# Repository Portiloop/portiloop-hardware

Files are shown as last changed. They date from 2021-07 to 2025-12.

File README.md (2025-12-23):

# Portiloop hardware

This repository documents hardware implementations of the `Portiloop` device. 
Which is a portable EEG closed-loop stimulation device.
[The software repository](https://github.com/Portiloop/portiloop-software) enables controlling the device from a simple Graphical User Interface (GUI).

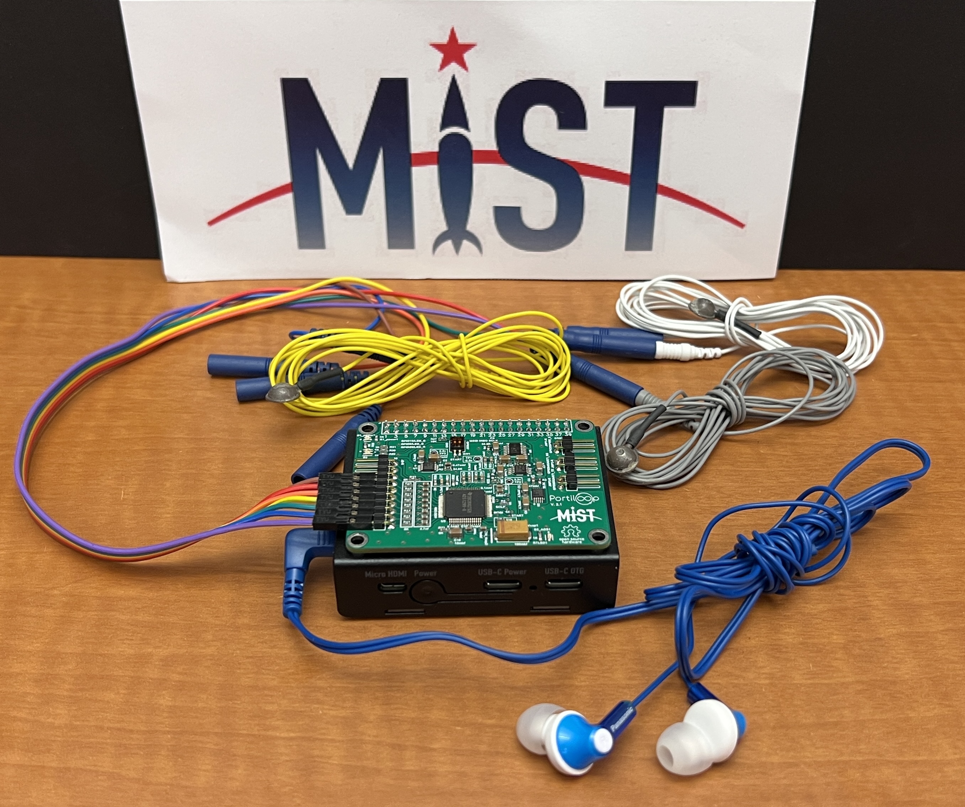
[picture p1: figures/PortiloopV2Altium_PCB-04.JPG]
mainImage


The last hardware iteration of the `Portiloop` device consists of a PCB built around an [ADS1299 chip](https://www.ti.com/product/ADS1299) 
with connectors for a [Coral Dev Board Mini](https://coral.ai/products/dev-board-mini/#documentation).
The `ADS1299` is an ADC responsible for processing analog EEG signal.

This repository open-sources all relevant plans for building this implementation.

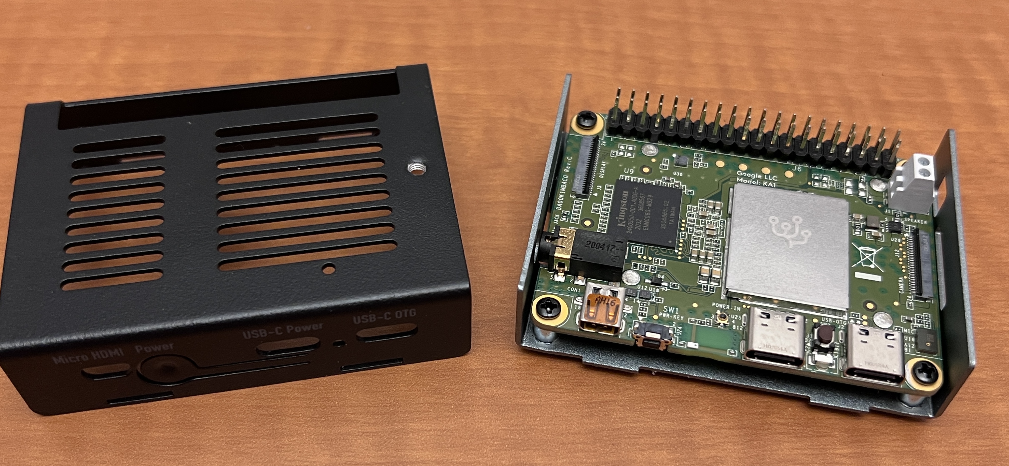
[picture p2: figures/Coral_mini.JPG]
coralMini

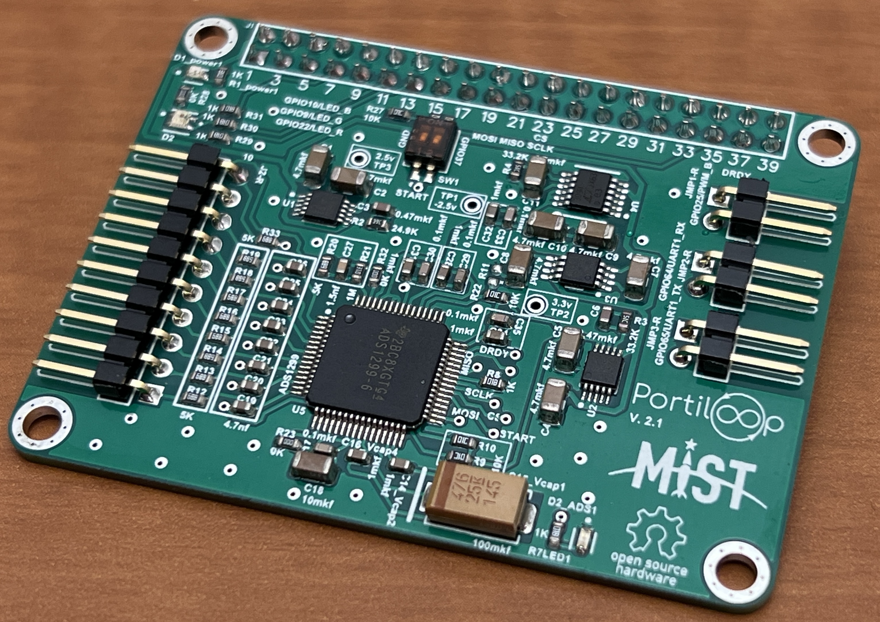
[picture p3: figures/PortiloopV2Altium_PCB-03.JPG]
v2.3

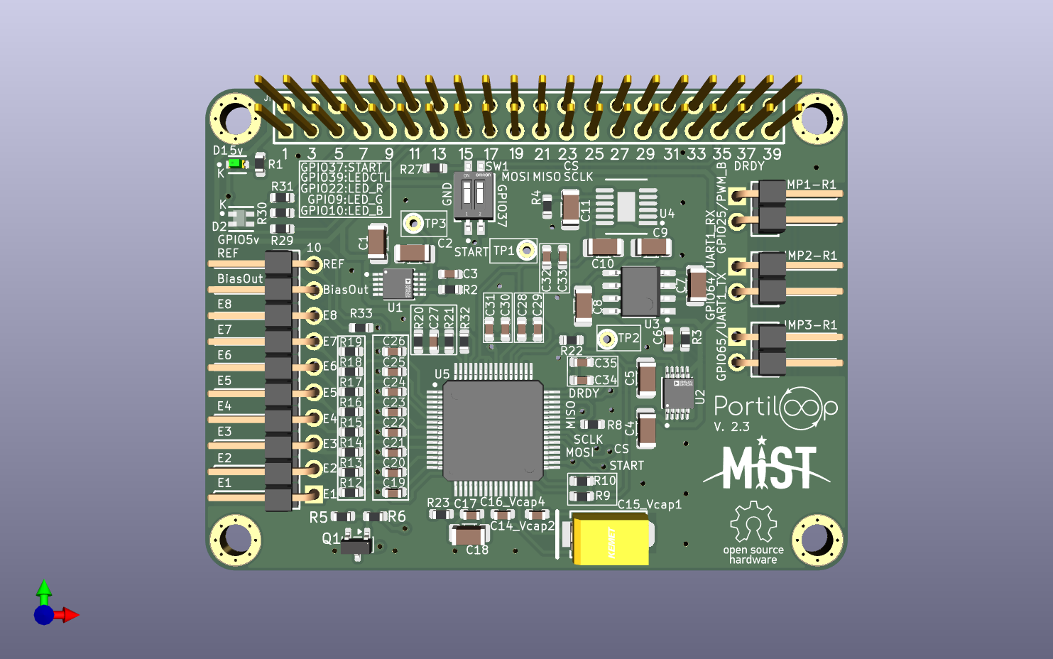
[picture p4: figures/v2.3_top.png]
top

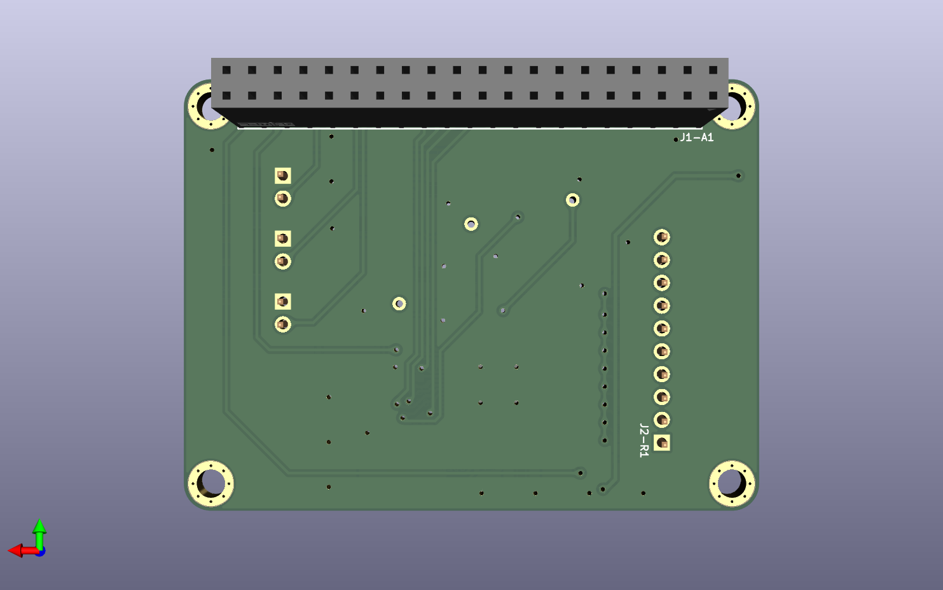
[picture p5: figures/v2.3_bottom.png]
back

video

To view the full interactive 3D model, click below:

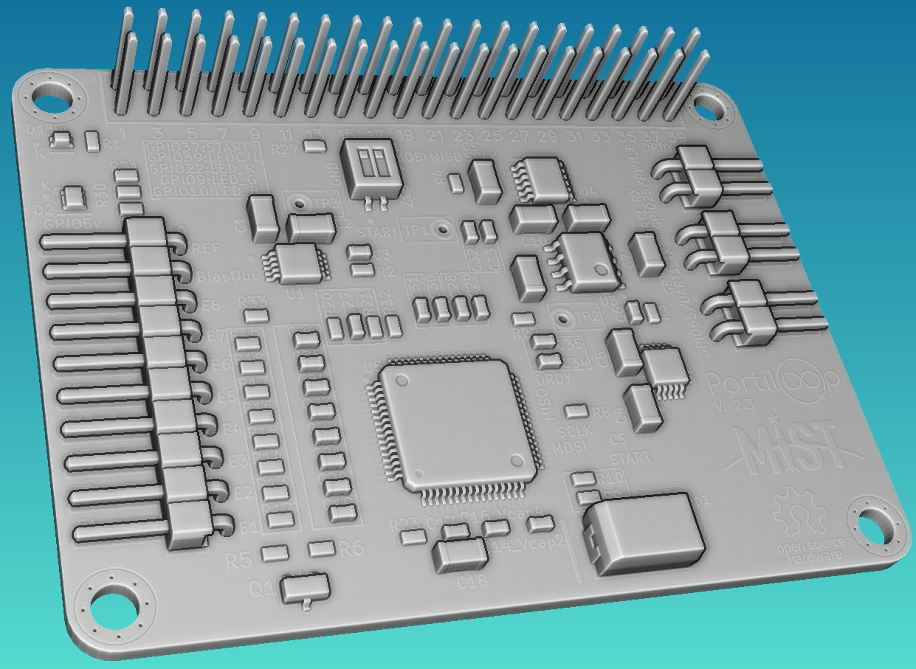
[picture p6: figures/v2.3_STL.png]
3D Preview Portiloop

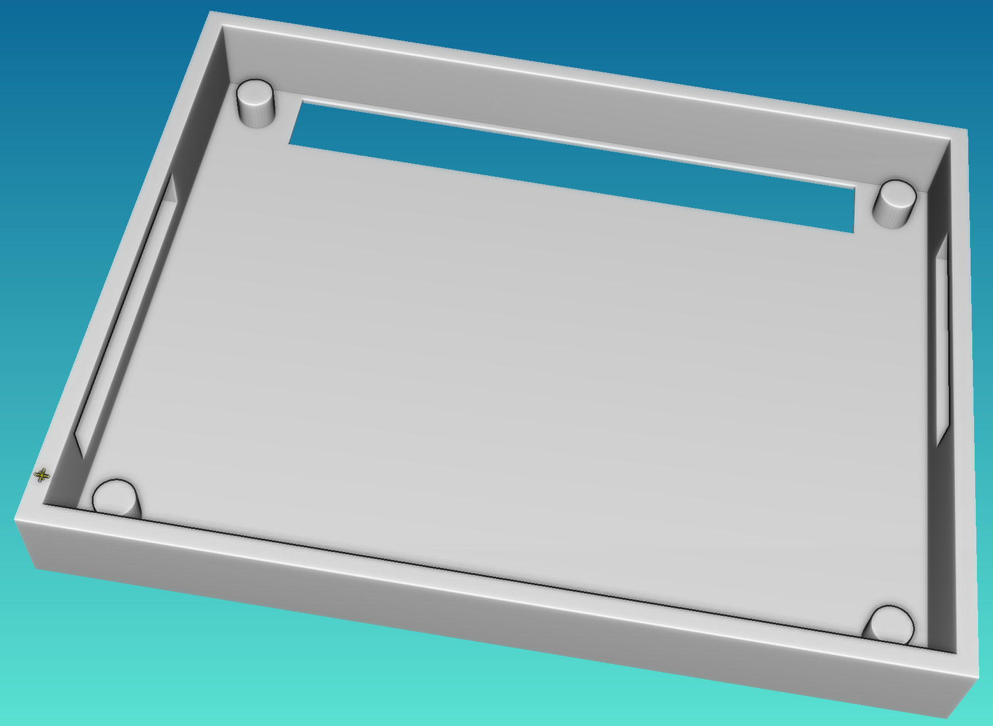
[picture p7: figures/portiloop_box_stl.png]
3D Preview Box

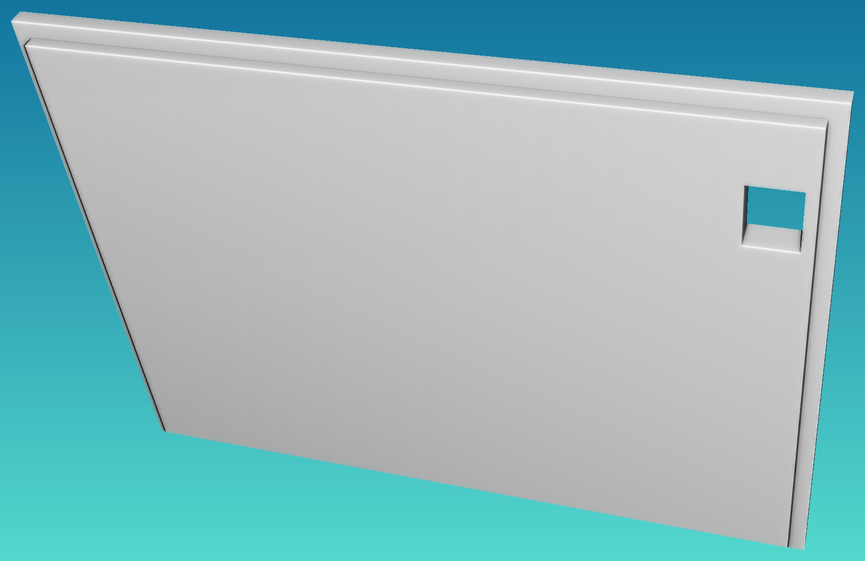
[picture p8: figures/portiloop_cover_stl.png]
3D Preview Box Cover

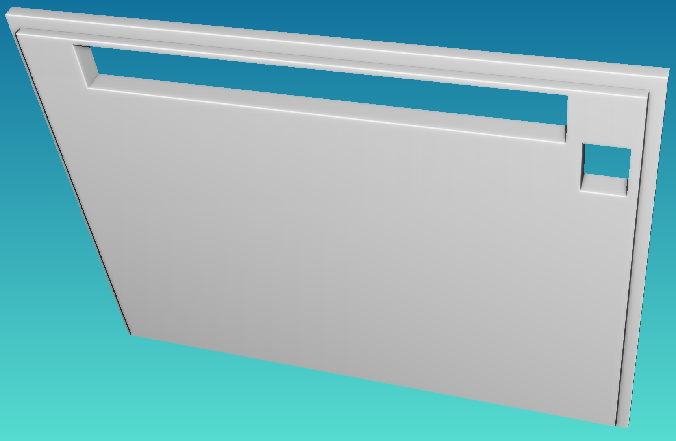
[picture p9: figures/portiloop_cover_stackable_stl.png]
3D Preview Box Cover Stackable


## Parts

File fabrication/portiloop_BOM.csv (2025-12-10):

Id | Designator | Footprint | Quantity | Designation | Part #
1 | C10,C1,C5,C4,C2,C9,C11 | 3216[1206]_cap | 7 | 4.7uF | CL31B475KBHNNNE
2 | C15_Vcap1 | KEMT-T491-D_M | 1 | 100uF | T491D107K016AT
3 | C16_Vcap4,C34,C31,C14_Vcap2,C32,C28 | 1608[0603]_cap | 6 | 1uF | CC0603KRX5R8BB105
4 | C18 | 3216[1206]_cap | 1 | 10uF | CC1206KKX7R8BB106
5 | C21,C26,C22,C20,C23,C19,C25,C24 | 1608[0603]_cap | 8 | 4.7nf | CC0603KRX7R9BB472
6 | C27 | 1608[0603]_cap | 1 | 1.5nf | CC0603KRX7R9BB152
7 | C35,C17,C33,C29,C30 | 1608[0603]_cap | 5 | 0.1uF | CC0603KRX7R9BB104
8 | C6,C3 | 1608[0603]_cap | 2 | 0.47uf | CC0603KRX7R9BB474
9 | C8,C7 | 3216[1206]_cap | 2 | 47uF | GRM31CR60J476ME19L
10 | D2 | FP-APTF1616SEJ3ZGGVBDC-MFG | 1 | APTF1616SEJ3ZGGVBDC
11 | D1 | FP-LTST-C190GKT-MFG | 1 | LTST-C190GKT
12 | J1-A1 | FP-SSQ-120-03-G-D-MFG | 1 | SSQ-120-03-G-D
13 | J2-R1 | 61301011021 | 1 | 61301011021
14 | JMP1-R1,JMP2-R1,JMP3-R1 | 61300211021 | 3 | 61300211021
15 | M2,M4,M3,M1 | board_screw | 4 | DNP | DNP
16 | Q1 | SOT-23 | 1 | IRLML2502 | IRLML2502TRPBF
17 | R1 | 1608[0603]_res | 1 | 1K | RC0603FR-071KL
18 | R12,R19,R33,R14,R18,R20,R16,R17,R15,R13 | 1608[0603]_res | 10 | 5K OR 4.99K | RC0603FR-074K99L
19 | R21 | 1608[0603]_res | 1 | 1M | RC0603FR-071ML
20 | R29 | 1608[0603]_res | 1 | 1.5K | RC0603FR-071K5L
21 | R3 | 1608[0603]_res | 1 | 33.2K | RC0603FR-0733K2L
22 | R30 | 1608[0603]_res | 1 | 6K OR 6.04K | RC0603FR-076K04L
23 | R31 | 1608[0603]_res | 1 | 1.8K | RC0603FR-071K8L
24 | R32,R23 | 1608[0603]_res | 2 | 0 | RC0603FR-070RL
25 | R4,R2 | 1608[0603]_res | 2 | 24.9K | RC0603FR-0724K9L
26 | R5 | 1608[0603]_res | 1 | 100K | 0603SAJ0104T5E
27 | R6 | 1608[0603]_res | 1 | 100 | RC0603JR-07100RL
28 | R8,R9,R10,R22,R27 | 1608[0603]_res | 5 | 10K | RC0603FR-0710KL
29 | SW1 | FP-A6H-2102-MFG | 1 | A6H-2102
30 | TP1,TP2,TP3 | TESTPOINT | 1 | DNP | DNP
31 | U2,U1 | FP-MSE-10-05-08-1664-IPC_C | 2 | LT3042xMSE | LT3042EMSE#PBF
32 | U3 | D0008A_M | 1 | LM2662MX/NOPB | LM2662MX/NOPB
33 | U4 | FP-MSE-12-05-08-1666-IPC_A | 1 | LT3094xMSE | LT3094EMSE#PBF
34 | U5 | PAG0064A_M | 1 | ADS1299IPAG

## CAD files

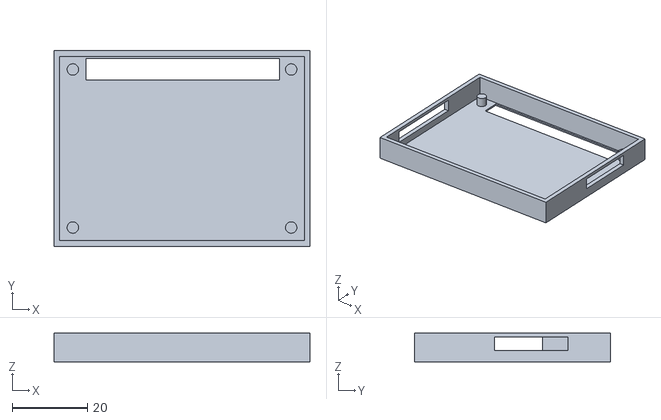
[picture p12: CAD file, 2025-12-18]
models/portiloop_box.stl
68.0 x 52.0 x 7.69

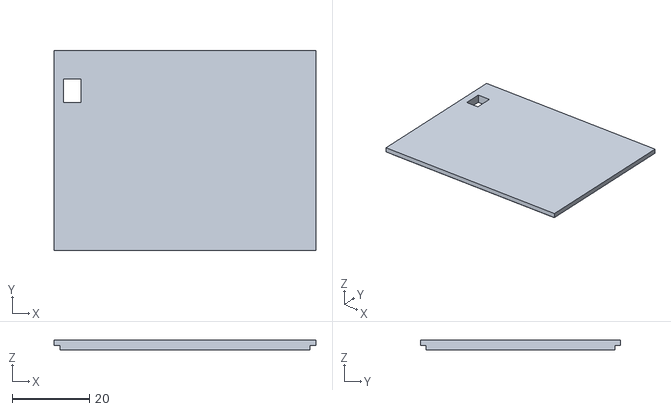
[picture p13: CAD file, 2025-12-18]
models/portiloop_cover.stl
68.0 x 52.0 x 2.65

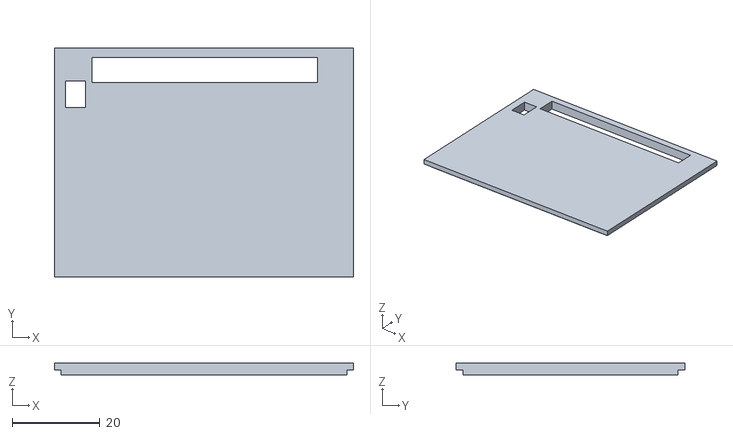
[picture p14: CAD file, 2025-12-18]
models/portiloop_cover_ stackable.stl
68.0 x 52.0 x 2.65

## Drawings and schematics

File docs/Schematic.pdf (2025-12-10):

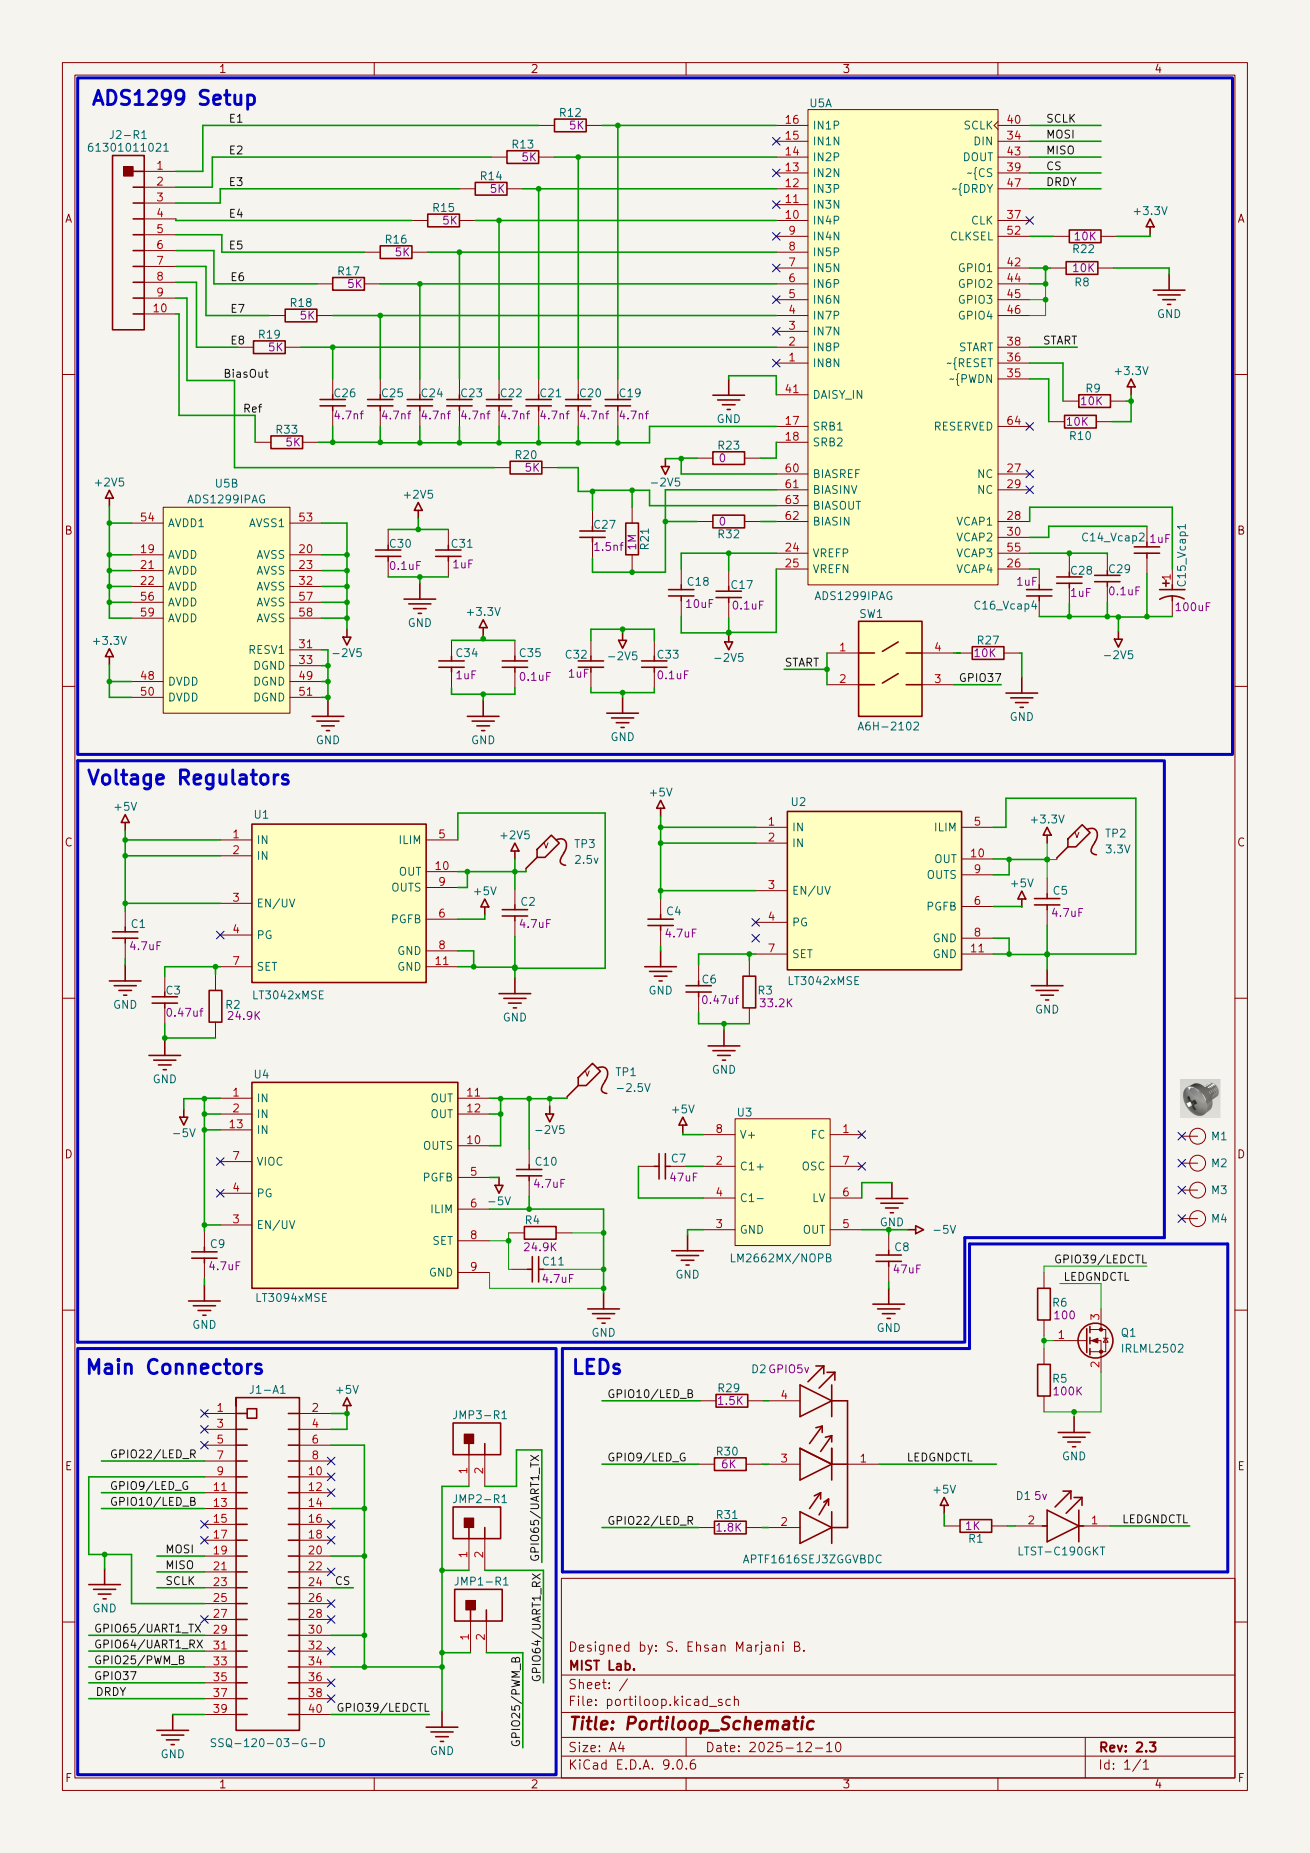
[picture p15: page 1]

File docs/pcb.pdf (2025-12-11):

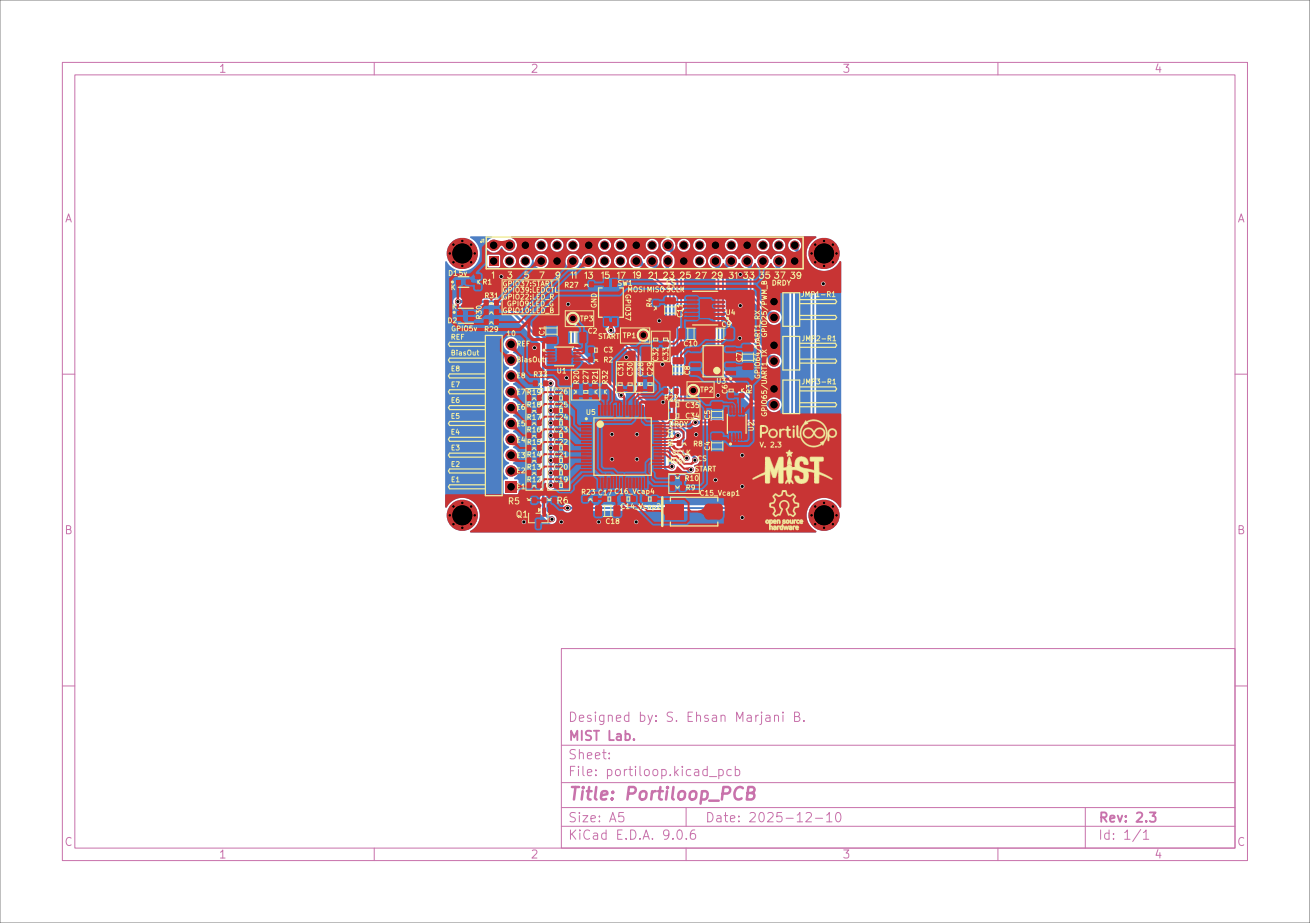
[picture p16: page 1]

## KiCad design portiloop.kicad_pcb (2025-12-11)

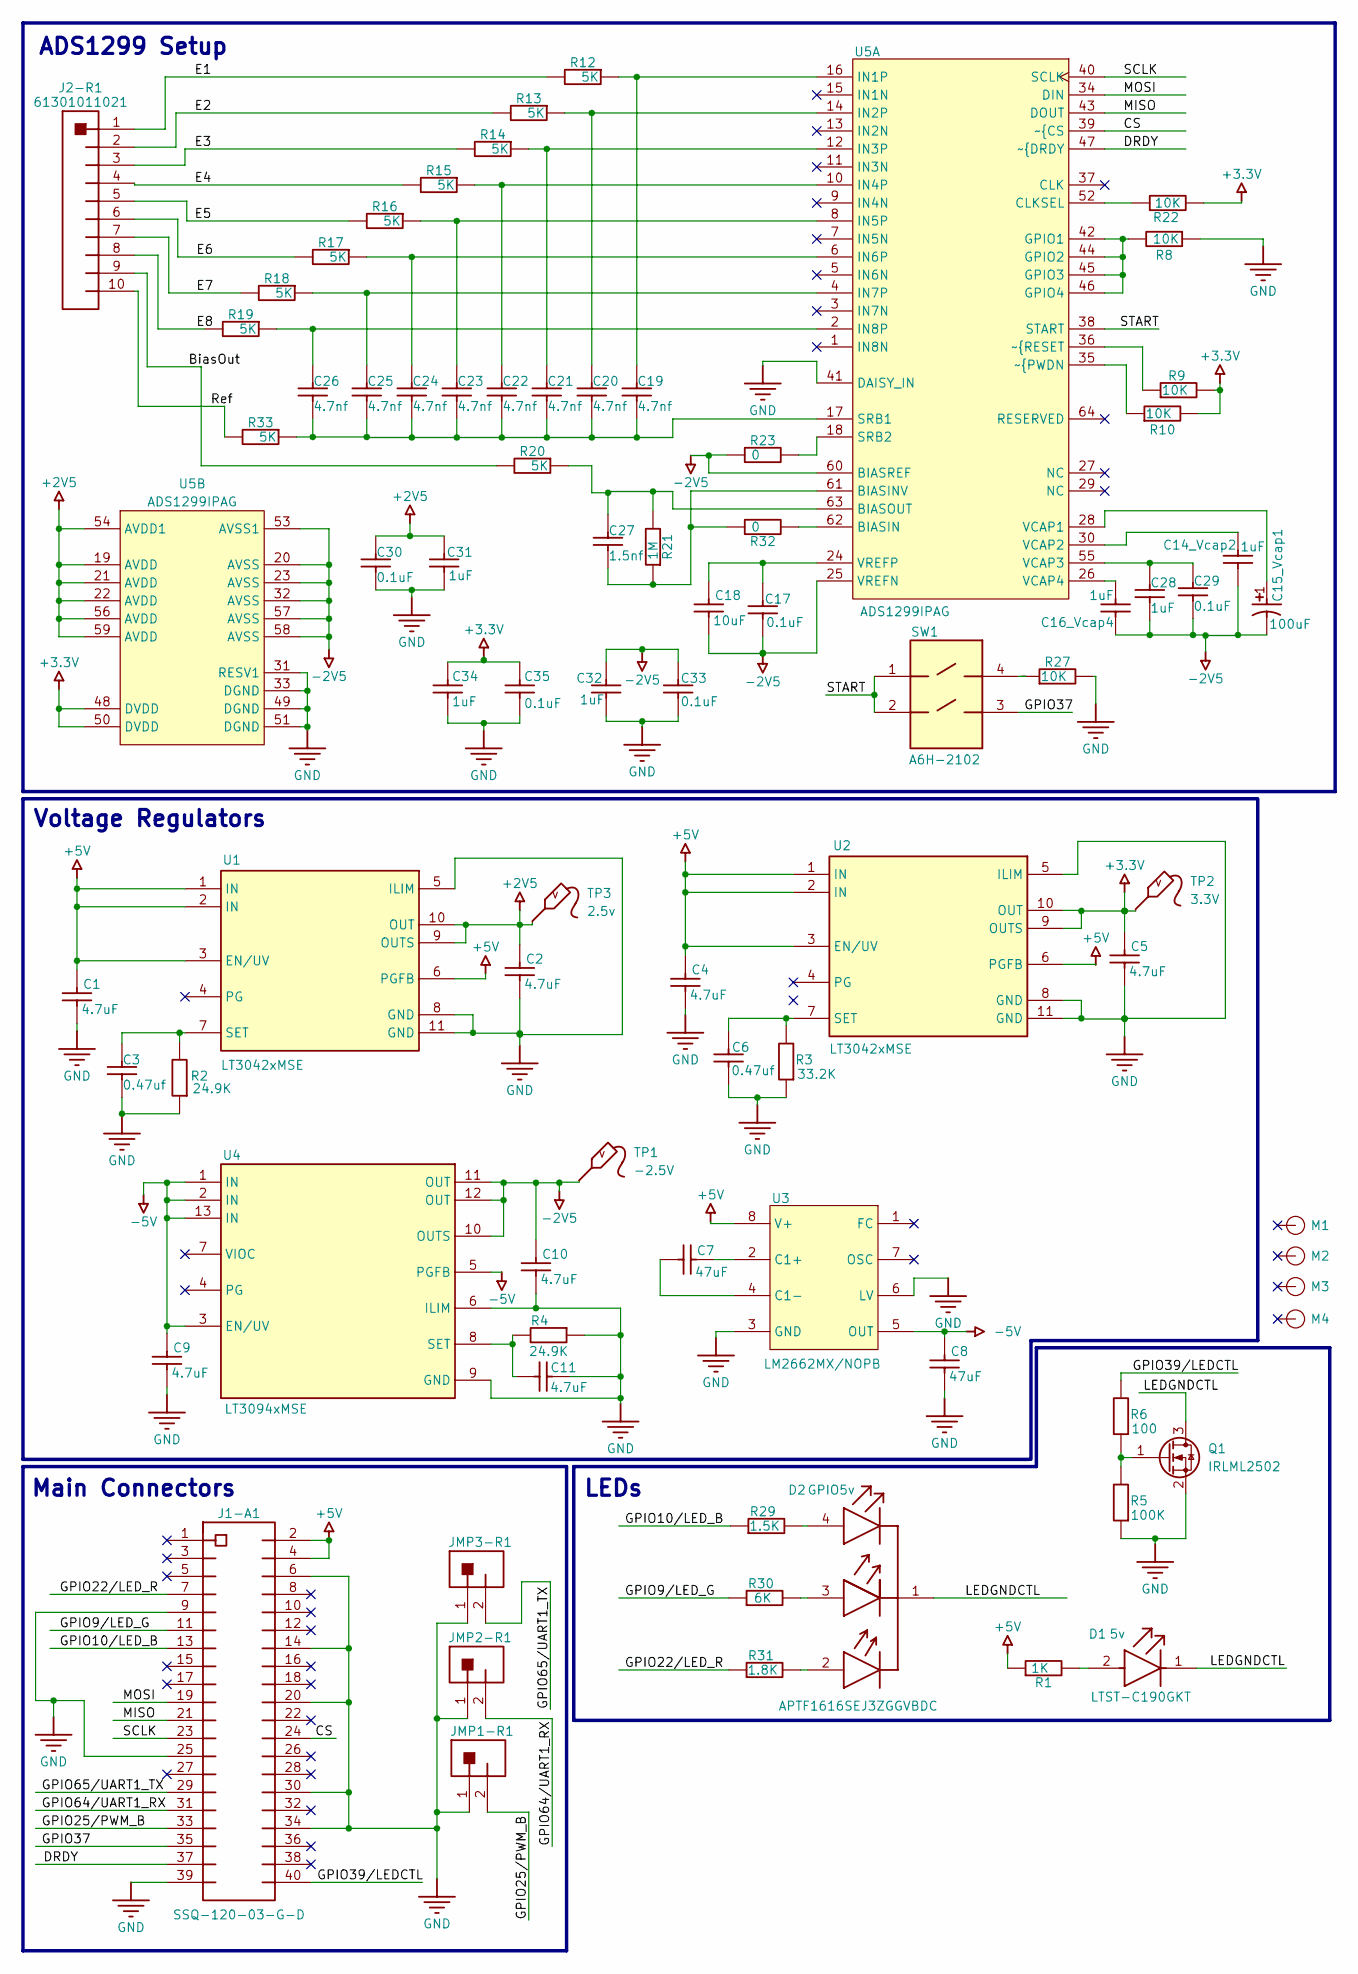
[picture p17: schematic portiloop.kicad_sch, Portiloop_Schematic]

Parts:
C1, C2, C4, C5, C9, C10, C11: 4.7uF; 3216[1206]_cap_3d
C3, C6: 0.47uf; 1608[0603]_cap_3d
C7, C8: 47uF; 3216[1206]_cap_3d
C14_Vcap2, C16_Vcap4, C28, C31, C32, C34: 1uF; 1608[0603]_cap_3d
C15_Vcap1: 100uF; KEMT-T491-D_M
C17, C29, C30, C33, C35: 0.1uF; 1608[0603]_cap_3d
C18: 10uF; 3216[1206]_cap_3d
C19, C20, C21, C22, C23, C24, C25, C26: 4.7nf; 1608[0603]_cap_3d
C27: 1.5nf; 1608[0603]_cap_3d
D1: LTST-C190GKT; FP-LTST-C190GKT-MFG
D2: APTF1616SEJ3ZGGVBDC; FP-APTF1616SEJ3ZGGVBDC-MFG
J1-A1: SSQ-120-03-G-D; FP-SSQ-120-03-G-D-MFG
J2-R1: 61301011021
JMP1-R1, JMP2-R1, JMP3-R1: 61300211021
M1, M2, M3, M4: board_screw
Q1: IRLML2502; SOT-23
R1: 1K; 1608[0603]_res_3d
R2, R4: 24.9K; 1608[0603]_res_3d
R3: 33.2K; 1608[0603]_res_3d
R5: 100K; 1608[0603]_res_3d
R6: 100; 1608[0603]_res_3d
R8, R22: 10k; 1608[0603]_res_3d
R9, R10, R27: 10K; 1608[0603]_res_3d
R12, R13, R14, R15, R16, R17, R18, R19, R20, R33: 5k; 1608[0603]_res_3d
R21: 1M; 1608[0603]_res_3d
R23, R32: 0; 1608[0603]_res_3d
R29: 1.5K; 1608[0603]_res_3d
R30: 6K; 1608[0603]_res_3d
R31: 1.8K; 1608[0603]_res_3d
SW1: A6H-2102; FP-A6H-2102-MFG
TP1: -2.5V; TESTPOINT
TP2: 3.3V; TESTPOINT
TP3: 2.5v; TESTPOINT
U1, U2: LT3042xMSE; FP-MSE-10-05-08-1664-IPC_C
U3: LM2662MX/NOPB; D0008A_M
U4: LT3094xMSE; FP-MSE-12-05-08-1666-IPC_A
U5: ADS1299IPAG; PAG0064A_M

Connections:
+2V5: C2.2, C30.2, C31.2, TP3.1 (T), U1.9 (OUTS), U1.10 (OUT), U5.19 (AVDD), U5.21 (AVDD), U5.22 (AVDD), U5.54 (AVDD1), U5.56 (AVDD), U5.59 (AVDD)
+3.3V: C5.2, C34.2, C35.2, R9.1, R10.1, R22.1, TP2.1 (T), U2.9 (OUTS), U2.10 (OUT), U5.48 (DVDD), U5.50 (DVDD)
+5V: C1.2, C4.2, J1-A1.2, J1-A1.4, R1.2, U1.1 (IN), U1.2 (IN), U1.3 (EN/UV), U1.6 (PGFB), U2.1 (IN), U2.2 (IN), U2.3 (EN/UV), U2.6 (PGFB), U3.8 (V+)
-2V5: C10.2, C14_Vcap2.1, C15_Vcap1.2, C16_Vcap4.1, C17.2, C18.1, C28.1, C29.1, C32.2, C33.2, R23.2, TP1.1 (T), U4.10 (OUTS), U4.11 (OUT), U4.12 (OUT), U5.20 (AVSS), U5.23 (AVSS), U5.25 (VREFN), U5.32 (AVSS), U5.53 (AVSS1), U5.57 (AVSS), U5.58 (AVSS), U5.60 (BIASREF)
-5V: C8.2, C9.2, U3.5 (OUT), U4.1 (IN), U4.2 (IN), U4.3 (EN/UV), U4.5 (PGFB), U4.13 (IN)
/BiasOut: J2-R1.9, R20.1
/CS: J1-A1.24, U5.39 (~{CS)
/DRDY: J1-A1.37, U5.47 (~{DRDY)
/E1: J2-R1.1, R12.1
/E2: J2-R1.2, R13.1
/E3: J2-R1.3, R14.1
/E4: J2-R1.4, R15.1
/E5: J2-R1.5, R16.1
/E6: J2-R1.6, R17.1
/E7: J2-R1.7, R18.1
/E8: J2-R1.8, R19.1
/GPIO9/LED_G: J1-A1.11, R30.2
/GPIO10/LED_B: J1-A1.13, R29.2
/GPIO22/LED_R: J1-A1.7, R31.2
/GPIO25/PWM_B: J1-A1.33, JMP1-R1.2
/GPIO37: J1-A1.35, SW1.3
/GPIO39/LEDCTL: J1-A1.40, R6.1
/GPIO64/UART1_RX: J1-A1.31, JMP2-R1.2
/GPIO65/UART1_TX: J1-A1.29, JMP3-R1.2
/LEDGNDCTL: D1.1 (C), D2.1 (COMMON_CATHODE), Q1.3 (D)
/MISO: J1-A1.21, U5.43 (DOUT)
/MOSI: J1-A1.19, U5.34 (DIN)
/Ref: J2-R1.10, R33.1
/SCLK: J1-A1.23, U5.40 (SCLK)
/START: SW1.1, SW1.2, U5.38 (START)
GND: C1.1, C2.1, C3.1, C4.1, C5.1, C6.2, C8.1, C9.1, C10.1, C11.1, C30.1, C31.1, C32.1, C33.1, C34.1, C35.1, J1-A1.6, J1-A1.9, J1-A1.14, J1-A1.20, J1-A1.25, J1-A1.30, J1-A1.34, J1-A1.39, JMP1-R1.1, JMP2-R1.1, JMP3-R1.1, Q1.2 (S), R2.2, R3.2, R4.2, R5.2, R8.2, R27.1, U1.5 (ILIM), U1.8 (GND), U1.11 (GND), U2.5 (ILIM), U2.8 (GND), U2.11 (GND), U3.3 (GND), U3.6 (LV), U4.6 (ILIM), U4.9 (GND), U5.31 (RESV1), U5.33 (DGND), U5.41 (DAISY_IN), U5.49 (DGND), U5.51 (DGND)
unnamed: D1.2 (A), R1.1
unnamed: D2.4 (BLUE_A), R29.1
unnamed: D2.3 (GREEN_A), R30.1
unnamed: D2.2 (RED_A), R31.1
unnamed: Q1.1 (G), R5.1, R6.2
unnamed: R27.2, SW1.4
unnamed: C3.2, R2.1, U1.7 (SET)
unnamed: C6.1, R3.1, U2.7 (SET)
unnamed: C7.2, U3.2 (C1+)
unnamed: C7.1, U3.4 (C1-)
unnamed: C11.2, R4.1, U4.8 (SET)
unnamed: R32.1, U5.62 (BIASIN)
unnamed: C27.1, R21.2, R32.2, U5.61 (BIASINV)
unnamed: C27.2, R20.2, R21.1, U5.63 (BIASOUT)
unnamed: R22.2, U5.52 (CLKSEL)
unnamed: R8.1, U5.42 (GPIO1), U5.44 (GPIO2), U5.45 (GPIO3), U5.46 (GPIO4)
unnamed: C19.2, R12.2, U5.16 (IN1P)
unnamed: C20.2, R13.2, U5.14 (IN2P)
unnamed: C21.2, R14.2, U5.12 (IN3P)
unnamed: C22.2, R15.2, U5.10 (IN4P)
unnamed: C23.2, R16.2, U5.8 (IN5P)
unnamed: C24.2, R17.2, U5.6 (IN6P)
unnamed: C25.2, R18.2, U5.4 (IN7P)
unnamed: C26.2, R19.2, U5.2 (IN8P)
unnamed: C19.1, C20.1, C21.1, C22.1, C23.1, C24.1, C25.1, C26.1, R33.2, U5.17 (SRB1)
unnamed: R23.1, U5.18 (SRB2)
unnamed: C15_Vcap1.1, U5.28 (VCAP1)
unnamed: C14_Vcap2.2, U5.30 (VCAP2)
unnamed: C28.2, C29.2, U5.55 (VCAP3)
unnamed: C16_Vcap4.2, U5.26 (VCAP4)
unnamed: C17.1, C18.2, U5.24 (VREFP)
unnamed: R10.2, U5.35 (~{PWDN)
unnamed: R9.2, U5.36 (~{RESET)

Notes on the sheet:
Voltage Regulators
ADS1299 Setup
LEDs
Main Connectors

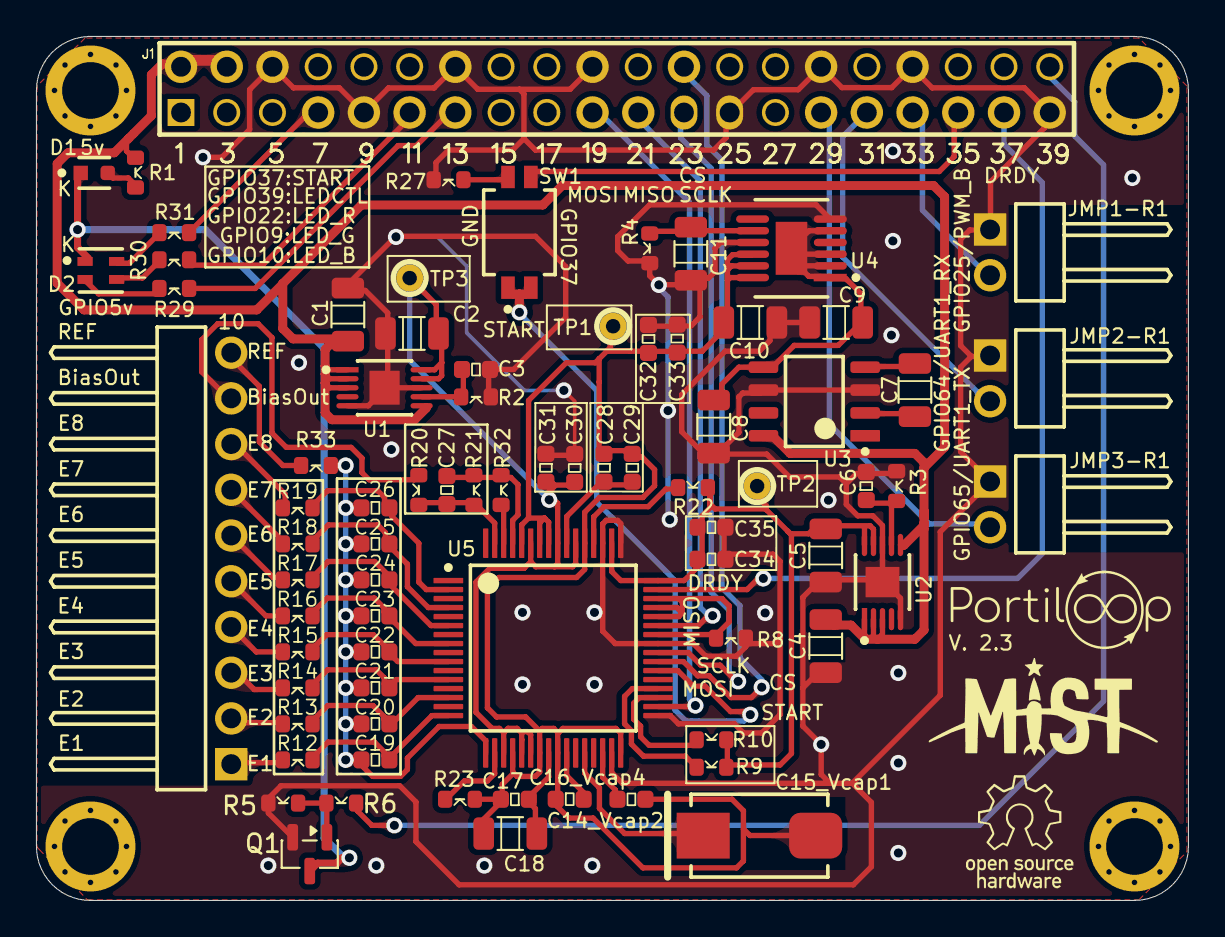
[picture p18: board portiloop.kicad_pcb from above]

Board: 2 copper layers, 64.0 x 48.0 mm, 81 parts (1 on the bottom side), 64 nets.

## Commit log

2021-07-21 Initial commit :rocket:
    [0V85.sch, 1V8.sch, 5V25.sch, ADAU1777BCBZRL.step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]
2021-07-22 Hooked-up the SoM
    [Coral-SoM.sch, EEG.sch, SD.sch, USB.sch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]
2021-07-26 Finish schematic and create interface specifications
    [5V25.sch, Coral-SoM.sch, EEG.sch, NX5427001Z.step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]
2021-07-27 Place components
    [SoM-power.sch, mist-eeg.kicad_pcb]
2021-07-28 Advance routing
    [5V25.sch, Coral-SoM.sch, EEG.sch, SD-power.sch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]
2021-07-29 Finished layout
    [mist-eeg.kicad_pcb]
2021-07-29 Fix text size in silkscreen
    [mist-eeg.kicad_pcb]
2021-07-29 Finish silkscreen
    [mist-eeg.kicad_pcb]
2021-07-30 Validation & fabrication layer
    [5V25.sch, EEG.sch, SD-power.sch, SD.sch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]
2021-08-02 Update footprints based upon piece availability & generate manufacturing files
    [5V25.sch, BOM.csv, EEG.sch, SD-power.sch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]
2021-08-02 Small fix to the TPS63070 footprint
    [Coral-SoM.sch, mist-eeg-B_Cu.gbr, mist-eeg-B_Mask.gbr, mist-eeg-B_Paste.gbr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]
2021-08-03 Update output files for PCBWay
    [mist-eeg-B_Cu.gbl, mist-eeg-B_Mask.gbs, mist-eeg-B_Paste.gbp, mist-eeg-B_SilkS.gbo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]
2021-08-05 Change buckboost regulator used
    [5V25.sch, Coral-SoM.sch, EEG.sch, SD-power.sch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]
2021-08-05 Switch to POL switching regulator to accelerate production of the board
    [BOM.csv, Coral-SoM.sch, EEG.sch, SD.sch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]
2021-08-05 Add BoM
    [BOM.csv, EEG.sch, mist-eeg.kicad_pcb]
2021-08-06 Switch to bigger min via size
    [BOM.csv, mist-eeg-B_Cu.gbl, mist-eeg-B_Mask.gbs, mist-eeg-B_Paste.gbp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]
2021-08-06 Fix drill size for LTC2947 vias
    [mist-eeg-B_Cu.gbl, mist-eeg-B_Mask.gbs, mist-eeg-B_Paste.gbp, mist-eeg-B_SilkS.gbo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]
2021-08-30 Add U8 & connectors to BOM
    [BOM.csv, mist-eeg.kicad_pcb]
2022-06-02 Added case 3D file
    [Main case portiloop v1.f3d]
2023-02-24 Added portiloop V2 files
    [1206ZD475JAT2A.step, ADS1299.kicad_sch, BoardOutline.gbr, Bottom.gbr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]
2023-07-28 Upload V2.2
    [PortiloopV2Altium_Project.PrjPcb, PortiloopV2Altium_Sch.SchDoc]
2023-08-30 cleanup v1
    [0V85.sch, 1V8.sch, 5V25.sch, ADAU1777BCBZRL.step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]
2025-12-10 version v2.3 KiCad 9.0.6
    [PortiloopV2Altium_Project.PrjPcb, PortiloopV2Altium_Sch.SchDoc, TPS65086100 OTP Generator V2p5.xlsx, portiloop-all-POS.csv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]
2025-12-18 box added
    [portiloop_box.stl, portiloop_cover.stl, portiloop_cover_ stackable.stl]
2025-12-23 Restructure project directories
    [portiloop-Bottom Layer.gbr, portiloop-Bottom Overlay.gbr, portiloop-Bottom Paste.gbr, portiloop-Bottom Solder.gbr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]
